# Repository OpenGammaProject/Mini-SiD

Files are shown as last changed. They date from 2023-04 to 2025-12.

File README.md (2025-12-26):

<a href="https://certification.oshwa.org/at000007.html" title="Open Source Hardware Association Certificate">Open Source Hardware Association Certificate</a>

# Mini SiPM Driver (SiD) Board

**This is the latest hardware revision 4.x. For older revisions, please have a look at the [other branches](https://github.com/OpenGammaProject/Mini-SiD/branches). A comparison between the revision 3 and 4 hardware can be found [here on Hackaday](https://hackaday.io/project/188090-mini-sipm-driver-board/log/225429-revision-4-is-finally-here).**

**This project is on [Hackaday.io](https://hackaday.io/project/188090-mini-sipm-driver-board), where I also post project logs, progress updates and other announcements.**

Minimalistic board that allows you to quickly and easily utilize a silicon photomultiplier (SiPM) within your other projects. Supports a range of input voltages, has a digital (TTL) pulse output for the registered counts and a direct output for the SiPM pulses for easy expansion. Similar to the original [Open Gamma Detector](https://github.com/OpenGammaProject/Open-Gamma-Detector), but without any direct way to perform gamma spectroscopy.

<p align="center">
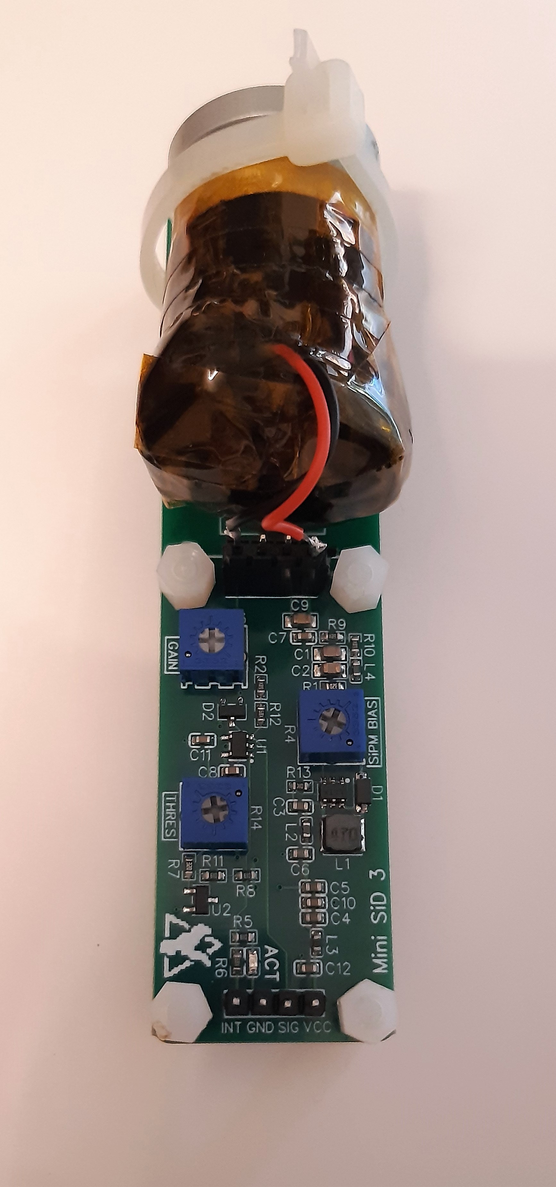
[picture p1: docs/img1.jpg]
  
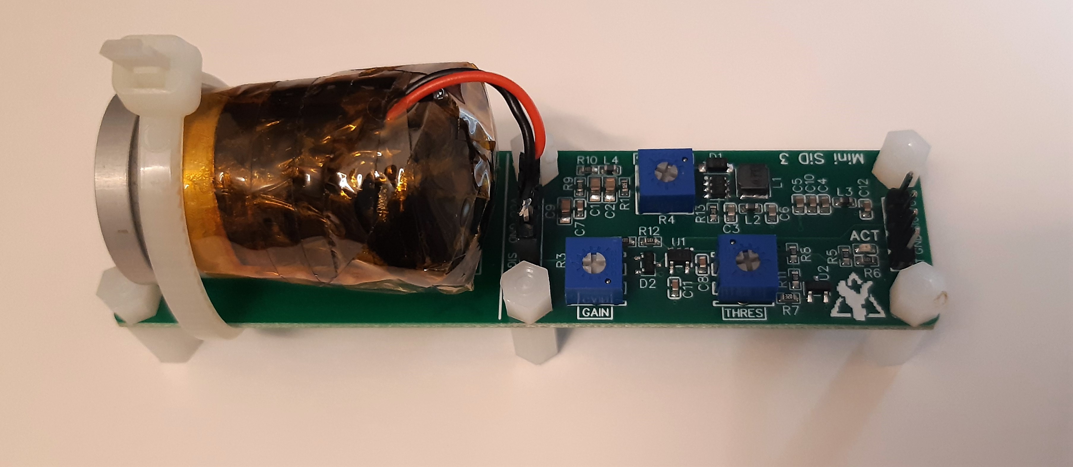
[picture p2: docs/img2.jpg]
  
</p>

All you need to build your own scintillation counter is this board, a scintillator and SiPM. The benefits of such a scintillation counter are that you can use it just like a Geiger counter, but it's much more sensitive, can be smaller, doesn't need 300+ Volts and you can also use it to do spectroscopy with some additional components. It mostly only registers gamma radiation though, so keep that in mind!



## How To Get One

PCB from PCBWay (https://www.pcbway.com/project/shareproject/Mini_SiPM_Driver_Mini_SiD_Board_110abc06.html)

* You can check out the project on PCBWay (affiliate) and if you buy through their service, it supports the project a little, and doesn’t cost you anything extra.
* Otherwise, use a PCB manufacturer and an electronics distributor of your choice and proceed on your own. All the files you'll need can be found in this repo.
* If you don't want to deal with all of that, feel free to contact me. Just send me an e-mail and I can help you out with the process.

**You will also need to buy a SiPM (e.g. the MICROFC-60035-SMT-TR) and scintillator (NaI(Tl) recommended) separately at a distributor of your choice.**

## Specifications

Here are some of the most important key facts:

* Compact design: Total size 100 x 25 mm. 50 x 25 mm area for electronics and additional 50 x 25 mm to mount a small scintillator.
* Input voltage: 3.1 V - 5.5 V.
* Low-voltage device: No HV needed like with a photomultiplier tube.
* SiPM voltage range from 27.5 V to 33.8 V.
* Low power consumption: <4 mA @ 5 V in standard operation.
* Adjustable gain for the SiPM pulses, also affects pulse decay time and therefore dead time.
* TTL output for counting pulses or time-over-threshold applications.
* Additional raw pulse output if you want to manipulate the signal or use it for spectroscopy.
* Dead time only limited by the speed of the scintillator and the gain. Typically only a few microseconds.
* Only needs an additional cheap microcontroller to, for example, build a simple scintillation counter.

## Working Principle

Here is a nice flow chart explaining how this device roughly works:

Working Principle Flow Chart

## Hardware

Hardware design has been done with [EasyEDA](https://easyeda.com/) and all the needed files for you to import the project as well as the schematic can be found in the `hardware` folder. There is also a Gerber file available for you to go directly to the PCB manufacturing step.

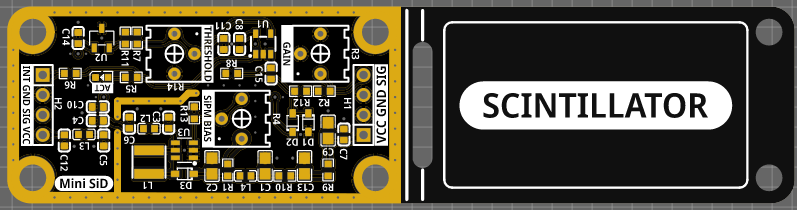
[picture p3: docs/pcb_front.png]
Front side rendering of the PCB


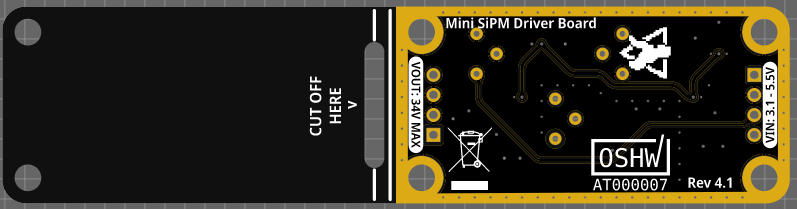
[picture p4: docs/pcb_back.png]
Back side rendering of the PCB


This project utilizes a silicon photomultiplier (short SiPM) which is way smaller and more robust than a traditional photomultiplier tube and does not need a high-voltage supply (traditionally  around 1000 V). Here are some very helpful in-depth datasheets about the particular MicroFC SiPM used here:

* [C-Series SiPM Sensors datasheet](https://www.onsemi.com/pdf/datasheet/microc-series-d.pdf)
* [Linearity of the Silicon Photomultiplier](https://www.onsemi.com/pub/Collateral/AND9776-D.PDF)
* [Introduction to the SiliconPhotomultiplier (SiPM)](https://www.onsemi.com/pub/Collateral/AND9770-D.PDF)
* [Biasing and Readout of ON Semiconductor SiPM Sensors](https://www.onsemi.com/pub/Collateral/AND9782-D.PDF)

PCB size is 10 x 2.5 cm. If you don't need the additional space to mechanically mount the SiPM/scintillator assembly to the rest of the detector board, you can just cut it off at the white line and you're left with a much smaller detector (~5.0 x 2.5 cm).

The PCB has four layers with components only at the top side. It mostly uses 0603 components or comparable IC packages to make it possible to solder it by hand and at the same time keep it as small as reasonable.
This combination makes for the best signal properties while still being fairly affordable with today's PCB manufacturing prices.

The TTL-compatible `INT` output is an active high pin!

**Here is a helpful image about the potentiometer settings (turning increases each setting):**

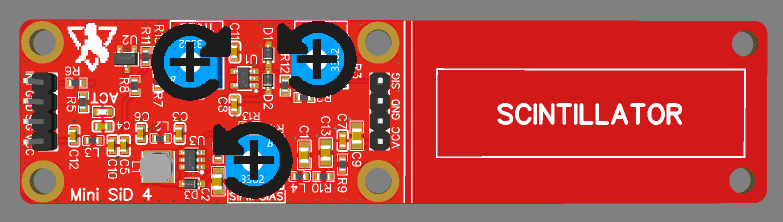
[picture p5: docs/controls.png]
Potentiometer Controls


## 3D Model

If you want to design an enclosure for the PCB or you need a 3D model for whatever other reason, you can have a look at the files in the `3D` folder. It includes 3D models of the PCB itself and some of the components on the board.

## Scintillation Counter

A great project utilizing the Mini SiD is building a scintillation counter, which can be much more powerful than a geiger counter while being safer to use, because of the relatively low voltages.

One great example build has been done by [RD-Gamma](https://rd-gammaspectra.xyz), who built one such device using a russian scintillator and a Broadcom AFBR SiPM.

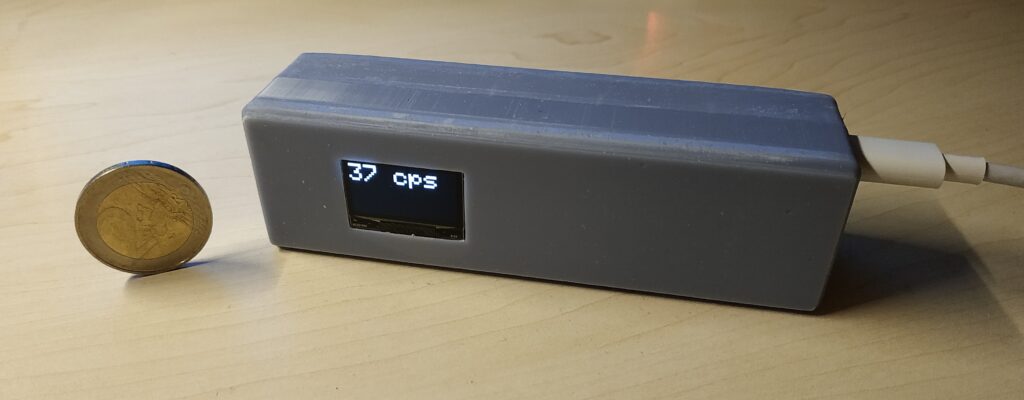
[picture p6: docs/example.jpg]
Photo of the DIY scintillation counter (https://rd-gammaspectra.xyz/?p=255)


## Example Results

Here is a small collection of example results I got when measuring the count rate at the TTL output with my small 18 x 30 mm NaI(Tl) scintillator and a 6 mm MicroFC SiPM.

| Sample | Result Average [cps] |
| --- | --- |
| Background (no source) | 24 |
| Am-241 (commonly used in ionization smoke detectors) | 230 |
| Cup with Uraninite glaze (i.e. containing natural pitchblende) | 64 |
| 5g LYSO scintillator (containing naturally-occuring Lu-176) | 34 |
| Thorianite (mineral) | 800 |

## Some Ideas

### Coincidence Measurements

You can tie multiple boards' `INT` outputs together in an `AND` gate chip to only trigger a signal when all boards detected something. These AND gate ICs are very cheap, readily available and the output can then go into a microcontroller interrupt pin to count the gamma events.

To make the timing a bit easier for the gates and to consider delays, you can feed the board `INT` output into a [monostable multivibrator circuit](https://en.wikipedia.org/wiki/Multivibrator#Monostable) such as an NE555 timer IC. This will allow you to stretch all the signals by a certain time factor you can set.

---

Thanks for reading.

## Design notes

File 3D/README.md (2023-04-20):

# 3D Model

This folder includes files for 3D modeling of and around the PCB and the components.

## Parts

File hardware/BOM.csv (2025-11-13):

You can find detailed documentation, photos, and example results there, along with links to project logs and community builds on Hackaday.io. | Name | Designator | Footprint | Quantity | Manufacturer Part | Manufacturer | Supplier | Supplier Part | Price
 | 10kΩ | R13,R15 | R0603 | 2 | 0603WAF1002T5E | UNI-ROYAL(厚声) | LCSC | C25804 | 0.001
Ordering your PCB through PCBWay helps support continued development of open-source radiation detection hardware. | 1kΩ | R5,R8 | R0603 | 2 | 0603WAF1001T5E | UNI-ROYAL(厚声) | LCSC | C21190 | 0.001
3 | 2kΩ | R3 | RES-ADJ-TH_3362P | 1 | 3362P-1-202LF | BOURNS | LCSC | C111654 | 0.373
4 | 50kΩ | R4,R14 | RES-ADJ-TH_3P-L7.1-W6.9-P2.50-L_3362P | 2 | 3362P-1-503 | BOCHEN(博晨) | LCSC | C118910 | 0.143
5 | 100nF | C7,C8,C10,C11,C12,C14,C15 | C0603 | 7 | CL10B104KC8NNNC | SAMSUNG(三星) | LCSC | C15725 | 0.006
6 | TLV3201AIDBVR | U1 | SOT-23-5_L3.0-W1.7-P0.95-LS2.8-BR | 1 | TLV3201AIDBVR | TI(德州仪器) | LCSC | C105188 | 0.403
7 | LTST-C190KGKT | ACT | LED0603-RD | 1 | LTST-C190KGKT | LITEON(光宝) | LCSC | C125094 | 0.015
8 | 49.9Ω | R2,R6,R9,R10,R12 | R0603 | 5 | 0603WAF499JT5E | UNI-ROYAL(厚声) | LCSC | C23185 | 0.001
9 | 4.7uF | C1,C2,C9,C13 | C0805 | 4 | CL21A475KBQNNNE | SAMSUNG(三星) | LCSC | C98192 | 0.02
10 | REF3030AIDBZR | U2 | SOT-23-3_L2.9-W1.6-P1.90-LS2.8-BR | 1 | REF3030AIDBZR | TI(德州仪器) | LCSC | C38423 | 0.263
11 | 210kΩ | R1,R7,R11 | R0603 | 3 | TC0325D2103T5H | UNI-ROYAL(厚声) | LCSC | C517422 | 0.023
12 | 22uF | C3,C4,C5,C6 | C0603 | 4 | CL10A226MP8NUNE | SAMSUNG(三星) | LCSC | C86295 | 0.015
13 | PMEG4010BEA | D1,D2,D3 | SOD-323_L1.8-W1.3-LS2.5-RD | 3 | PMEG4010BEA,115 | Nexperia(安世) | LCSC | C36975 | 1.315
14 | MTP125-1104S1 | H1,H2 | HDR-TH_4P-P2.54-V-M | 2 | MTP125-1104S1 | MINTRON(明硕) | LCSC | C358686 | 0.024
15 | 47uH | L1 | IND-SMD_L4.0-W4.0_NR4018T | 1 | NRS4018T470MDGJ | TAIYO YUDEN(太诱) | LCSC | C222886 | 0.126
16 | 1kΩ | L2,L3,L4 | L0603 | 3 | BLM18KG102SN1D | muRata(村田) | LCSC | C160982 | 0.017
17 | MAX5026EUT+T | U3 | SOT-23-6_L2.9-W1.6-P0.95-LS2.8-BL | 1 | MAX5026EUT+T | ADI(亚德诺)/MAXIM(美信) | LCSC | C87603 | 1.696

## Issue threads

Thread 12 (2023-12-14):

### ISSUE TITLE
MAX5026EUT+T replacement

### ISSUE THREAD

**Issue by dr4kan** [OpenGammaProject/Mini-SiD#12]
Hi,

first of all thank you for making available this project. I am interested in buying one assembled pcb to play with, so I tried to use jlcpcb.com. However, it looks like the MAX5026EUT+T is unavailable not only there, but also on lcsc.com. How can it be replaced without changing the design of the pcb?

Thanks

**Comment by NuclearPhoenixx** [comment]
Hi,

just use another distributor. Let JLCPCB assemble everything but the MAX5026 and then just order and solder that part for yourself.
You can get it pretty easily elsewhere, e.g. on mouser or digikey:
- https://www.mouser.at/ProductDetail/Analog-Devices-Maxim-Integrated/MAX5026EUT%2bT?qs=Mqkh4jHMT8zfiFUMsw6rrA%3D%3D
- https://www.digikey.at/de/products/detail/analog-devices-inc-maxim-integrated/MAX5026EUT-T/1516355?s=N4IgTCBcDaILIEEAaBWADGAbAUQKoBUBqfAAhAF0BfIA

I've even seen the MAX5026 sold on ebay at reasonable prices, so it really shouldn't be hard to get one :)

Hope that helps!

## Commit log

2022-11-15 add hardware files
    [BOM.csv, Drill_NPTH_Through.DRL, Drill_PTH_Through.DRL, Drill_PTH_Through_Via.DRL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]
2022-11-15 [ImgBot] Optimize images
    *Total -- 101.44kb -> 52.99kb (47.76%)
    /docs/flow.drawio.png -- 26.55kb -> 9.24kb (65.22%)
    /docs/pcb_back.png -- 24.58kb -> 14.06kb (42.81%)
    /docs/pcb_front.png -- 50.30kb -> 29.70kb (40.97%)
2022-11-16 fix Kitspace Gerber preview
    [Drill_NPTH_Through.DRL, Drill_PTH_Through.DRL, Drill_PTH_Through_Via.DRL, Gerber_BoardOutlineLayer.GKO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]
2022-12-04 minor fixes
    i didn't change much at all, just some documentation corrections and lib updates
    [BOM.csv, Drill_NPTH_Through.DRL, Drill_PTH_Through.DRL, Drill_PTH_Through_Via.DRL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]
2023-01-11 Stop filtering out PCB services in kitspace.yaml
2023-03-08 rev 3
    [BOM.csv, Drill_NPTH_Through.DRL, Drill_PTH_Through.DRL, Drill_PTH_Through_Via.DRL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]
2023-04-13 [ImgBot] Optimize images
    *Total -- 1,540.28kb -> 1,415.24kb (8.12%)
    /docs/pcb_back.png -- 26.67kb -> 16.69kb (37.41%)
    /docs/pcb_front.png -- 38.81kb -> 25.29kb (34.84%)
    /docs/flow.drawio.svg -- 17.03kb -> 15.71kb (7.73%)
    /docs/img1.jpg -- 789.83kb -> 733.40kb (7.14%)
    /docs/img2.jpg -- 665.08kb -> 621.37kb (6.57%)
    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
2023-04-19 Update OSHWA cert
    [Drill_NPTH_Through.DRL, Drill_PTH_Through.DRL, Drill_PTH_Through_Via.DRL, Gerber_BoardOutlineLayer.GKO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]
2023-04-19 [ImgBot] Optimize images
    *Total -- 29.92kb -> 14.30kb (52.22%)
    /docs/pcb_back.png -- 27.08kb -> 11.52kb (57.44%)
    /docs/oshw.svg -- 2.85kb -> 2.78kb (2.54%)
2023-05-17 Arduino UNO example
2023-11-22 upload rev 4
    [BOM.csv, Drill_NPTH_Through.DRL, Drill_PTH_Through.DRL, Drill_PTH_Through_Via.DRL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]
2023-11-22 Update PCB layer note
2023-11-29 add OSHWA cert
    [Drill_NPTH_Through.DRL, Drill_PTH_Through.DRL, Drill_PTH_Through_Via.DRL, Gerber_BoardOutlineLayer.GKO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]
2023-11-30 [ImgBot] Optimize images
    *Total -- 134.45kb -> 88.11kb (34.47%)
    /docs/controls.png -- 43.34kb -> 26.37kb (39.16%)
    /docs/pcb_back.png -- 30.82kb -> 19.54kb (36.59%)
    /docs/pcb_front.png -- 46.77kb -> 29.67kb (36.55%)
    /docs/oshw.svg -- 13.54kb -> 12.54kb (7.39%)
2024-03-01 add rev 4.1
    [BOM.csv, Drill_NPTH_Through.DRL, Drill_PTH_Through.DRL, Drill_PTH_Through_Via.DRL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]
2024-11-14 fix missing R15 from PCB
    Also pulled EasyEDA library updates for all components at the same time
    No functional changes
    [BOM.csv, Drill_NPTH_Through.DRL, Drill_PTH_Through.DRL, Drill_PTH_Through_Via.DRL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]
2025-02-22 add pick and place file
    [PickAndPlace_PCB.csv]
2025-06-18 [ImgBot] Optimize images
    *Total -- 247.05kb -> 210.13kb (14.95%)
    /docs/pcb_back.png -- 39.27kb -> 26.62kb (32.22%)
    /docs/pcb_front.png -- 68.54kb -> 46.86kb (31.64%)
    /docs/flow.drawio.svg -- 139.24kb -> 136.66kb (1.86%)
2025-11-13 fix project files
    [BOM.csv, Drill_NPTH_Through.DRL, Drill_PTH_Through.DRL, Drill_PTH_Through_Via.DRL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]
2025-11-13 add PCBWay affiliate
